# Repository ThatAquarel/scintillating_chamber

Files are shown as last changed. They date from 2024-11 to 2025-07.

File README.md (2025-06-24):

# [Dawson HEP](https://youtu.be/Yp-H1ZBjPuM)

Introduction Video:

Demo video (https://youtu.be/Yp-H1ZBjPuM)

## About us

Icons

**The Dawson High Energy Physics** club, run by Dr. Manuel Toharia Zapata is a place for curious college students to learn more about particle physics. Every week, students from a wide variety of programs meet to learn and discuss about flavour physisc, extra dimensions and much more. We engage with both theory and experiments, learning about and observing particles. Our many projects include an Alpha particle detector, spark chamber, Scintillating Chamber, and more.

Here's a [video](https://youtu.be/Yp-H1ZBjPuM) about our group!

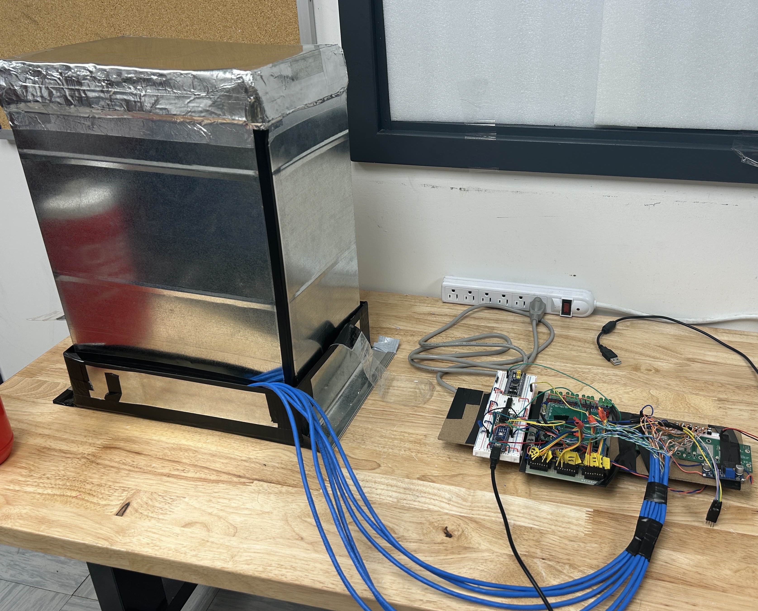
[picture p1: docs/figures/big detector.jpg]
Scintillating chamber


Our proposal to the 2025 [Beamline for schools](https://beamlineforschools.cern/) competition. It consists of an arrangement of scitillator rods to detect and model the trajectory of cosmic ray in three dimensions. The possible trajectories are then calculated and displayed graphically to the user.

**See Paper [HERE](./proposal/proposal.pdf)**

## Contacts

- Milo Belarbi
- David Birnbaum
- Tykhon Byshkin
- Matvey Chirchikov
- Danah Dézémé
- Arij Mohamedi
- [Evan Parasol](https://github.com/TheBookwyrms), blackdragon6493@gmail.com
- [Leandro Perez-Moran](https://github.com/LudioRex), pemle2007@gmail.com
- Ari Polterovich
- [Tian Yi, Xia](https://github.com/ThatAquarel), xtxiatianyi@gmail.com
- [Andy Yu](https://github.com/Anodymous1), andy.yu@dawsoncollege.qc.ca
- [Aljoscha Ziegler](https://github.com/Questionning), ziegleraljoscha@gmail.com

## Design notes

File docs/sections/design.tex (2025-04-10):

The general working principle of our detector is simple:
polyvinyl toluene (PVT) scintillator rods are arranged in
the detector, and when a muon passes through a rod, photons emitted are then detected by a Silicon Photomultiplier
(SiPM). The collected data is then transferred to a computer where the data is processed and rendered to display the possible paths of the muon. Our design strays from conventional detectors when it comes to the arrangement of the scintillator rods. While typical detectors use a grid design, we opted for a design inspired by binary encoding (see figure \ref{fig0}). 

\begin{figure}[h]
    \centering
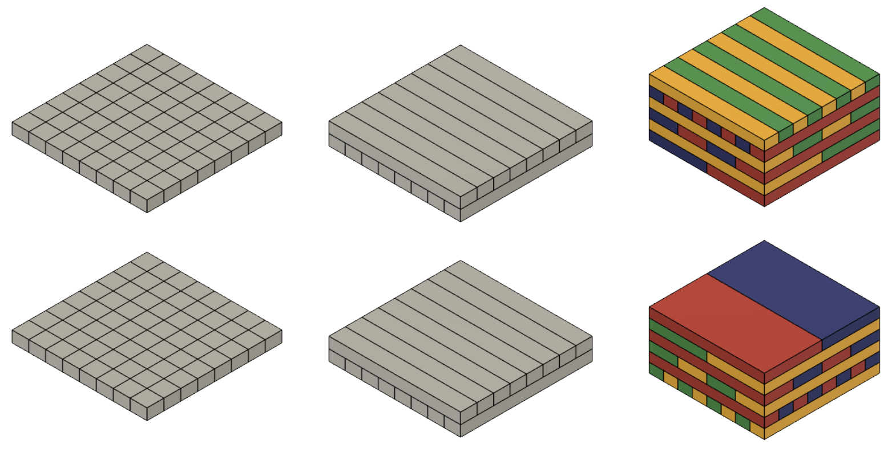
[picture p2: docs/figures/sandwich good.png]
    
\caption{Comparison of three scintillator placement methods: $n$ being the number of scintillators on the side of
one of the extreme layers. 
\textbf{Left:} One layer grid design. Number of sensors scale as $2n^2$.
\textbf{Middle:} Two layer grid design, scales as $4n$.
\textbf{Right:} Binary
encoding arrangement, number of required sensors scales as
$8 log_2(n)$. In each layer, identically coloured
scintillators are optically linked to the same SiPM by WLS
fiber.}
\label{fig0}
\end{figure}

This has two main benefits. First, it reduces the number of sensors needed, as only two sensors are necessary per layer. As such, the number of sensors needed for the detector increases logarithmically. Our design also allows for easy encoding of the detector’s state. With each layer only having two sensors, its state can be represented with a single bit, and because each layer is more specific than the previous, it narrows down the possible paths of the particle through the detector. Each set of signals therefore encodes for a specific pattern. This is analogous to the system used in the Apollo Guidance Computer’s rope core memory, with each bit representing an inhibit wire pair\cite{agc}.

\begin{figure}[h]
    \centering
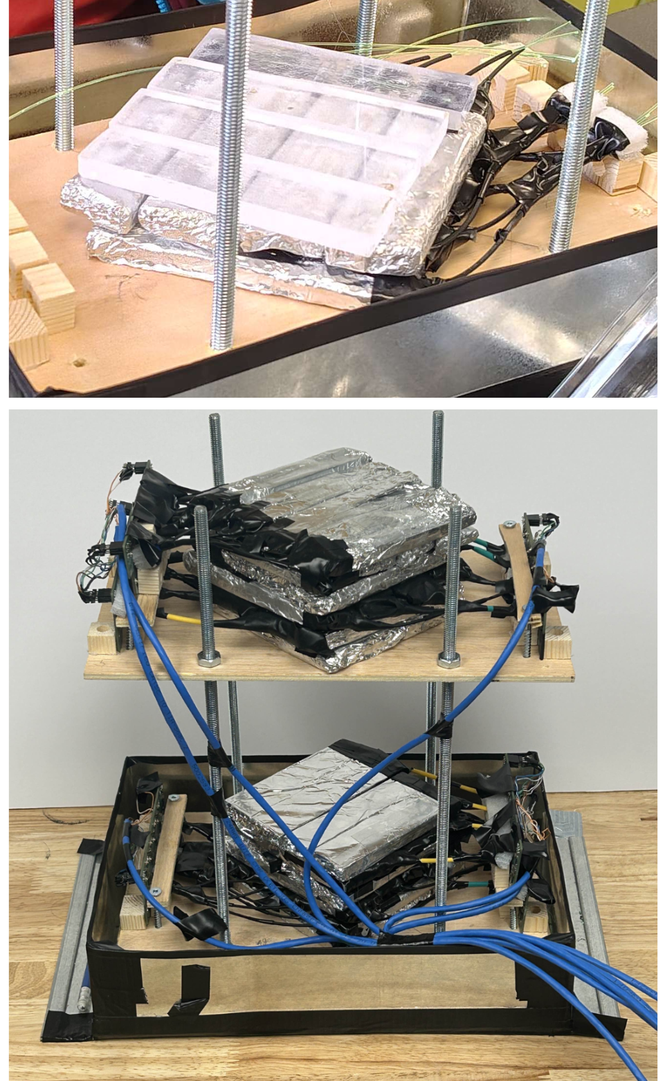
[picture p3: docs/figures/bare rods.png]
    
    \caption{Isometric view of physical detector. WLS fiber is encased within dark tubing toward the SiPM boards. Four threaded rods elevate the top platform: nuts allow for relative parallelism adjustment. Top and bottom scintillator packs permit the encoding of XY positioning; both combined, 3D trajectory tracking. A total of $12\,\text{layers} \times 2\,\text{SiPMs/layer} = 24\,\text{SiPMs}$.}
    \label{fig1}
\end{figure}

%\clearpage

\vspace{10mm}
In greater detail, each rod is optically isolated from its neighbors with aluminium foil and connected to a remote SiPM through wavelength shifting fiber (WLS fiber)\cite{wls} . We opted for WLS fiber, as is common among scintillation detectors, because it is more efficient at capturing the photons emitted by the scintillators than clear fibers. The output of the SiPMs being too weak, we use op-amp transimpedance amplifiers to amplify the signal. After being amplified, the signals are digitized before entering an FPGA circuit for fast acquisition \footnote{All circuits and PCBs are custom-made. Access the documentation \href{https://github.com/ThatAquarel/hep/tree/main/scintillator_field/hardware/docs}{\underline{here}}}. An Arduino then filters the signal before it is sent to a computer for processing.

\begin{figure}[h]
    \centering
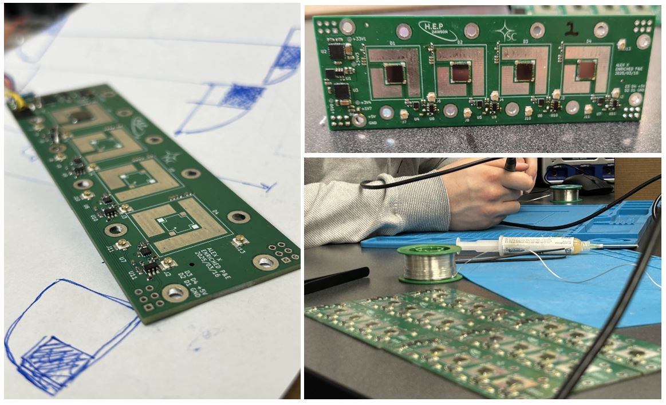
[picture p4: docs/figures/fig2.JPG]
    
\caption{Student-designed SiPM printed-circuit boards. Each PCB has four channels; a total of six PCBs are used in our detector. SiPMs and other components are manually populated onto the PCB.}
\label{fig2}
\end{figure}

%BIG BOX
\begin{figure} [h]
    \centering
    
    \caption{Binary optical encoding scintillation detector in its final form. \textbf{Left:} Light-tight faraday cage containing the detector made of HVAC conduit\textemdash decreasing light contamination and electrical noise. \textbf{Right:} Acquisition circuit linked with data cables.}
    \label{fig4}
\end{figure}

\vspace{15mm}
The trajectory volume\textemdash the possible volume of muon trajectory\textemdash is calculated in O(n) using Python code\footnote{All code can be found in our \href{https://github.com/ThatAquarel/hep}{\underline{GitHub repository}}.} by splitting the detector into two side-projections. The code calculates the trajectory volume projection for each side view by iterating over two levels at a time and conserving the tightest projection, first combining the center levels and finally the uppermost and lowermost levels. The volume trajectory projections are combined into the volume trajectory. Future updates will include : adapting to situations where the muon passed between two rods of the same level and taking advantage of situations where muons had to pass in between same level rods. 

\begin{figure}[h]
    \centering
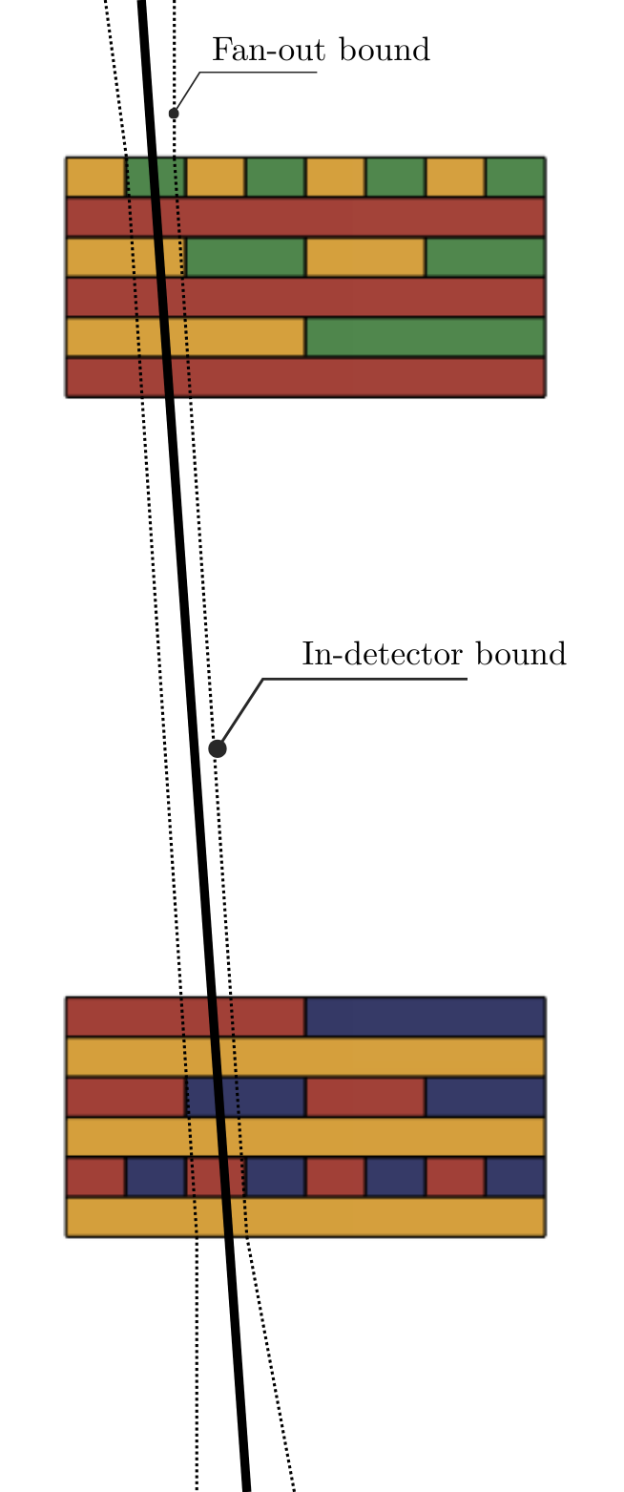
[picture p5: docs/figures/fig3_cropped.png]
    
    \caption{Representation of a possible muon trajectory and the calculated trajectory volume projection. Black line a possible muon path. Black dotted line is the side muon volume projection: boundaries for all possible muon paths.
}
    \label{fig3}
\end{figure}

The display is written in Python, using GLFW to create the display window, PyOpenGL to turn the coordinates from the muon volume trajectory into coordinates relevant to the computer, as well as to create the shaders, vertex arrays, and vertex buffers which are needed to render the scintillator structure and trajectory volume to the computer, and ImGui to create the text box that gives information to users.
\begin{figure}[h]
    \centering
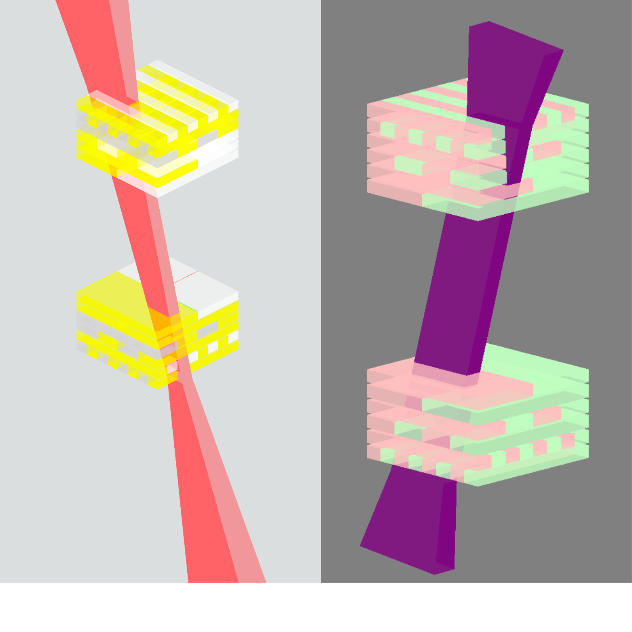
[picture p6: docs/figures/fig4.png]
    
    \caption{Two experimental instances of isometric views of binary positional decoding by our software from real data. \textbf{Left:} Signals sent to the computer are interpreted visually. \textbf{\textit{Yellow:}} Triggered scintillators. \textbf{\textit{White:}} Untriggered scintillators. \textbf{\textit{Red:}} Volume of possible muon trajectory resulting from binary elimination of trajectories. \textbf{Right:} More efficient render without signal interpretation. \textbf{\textit{Purple:}} Volume of possible muon trajectories.}
    \label{fig4}
\end{figure}

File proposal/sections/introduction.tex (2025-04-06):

At any given moment, there are muons raining down on us at a rate of approximately 1 muon per square centimeter per minute [1]. Traditionally, they are observed with the use of a spark chamber. However, building a spark chamber is a technical challenge, especially for high school students. We wanted to create a simple and easily reproducible way of observing muons, which is what led us to develop our three-dimensional scintillator-based detector, a.k.a. The Scintillating Chamber. Although we have developed the detector’s software and hardware components, precise calibration would require exposure to a controlled muon beam. Access to CERN’s world-class facilities would allow us to validate our detector’s performance and refine its accuracy. It would also provide invaluable insights into innovative techniques that would contribute to the broader field of particle detection technology. We hope to collaborate with peers and experts at CERN to deepen our comprehension of physics concepts through real-world applications. We are also committed to inspiring other young Canadian scientists by sharing our experiences and findings through outreach activities. An opportunity to conduct our experiment at CERN would be a pivotal step in this journey. We hope that our design can be used in physics classrooms around the world to assist science education and communication. Our team hopes to continue development to enhance our detector for these purposes, adding a timing device to measure the energy of the detected particles, and creating a better user interface for easier use in classrooms.

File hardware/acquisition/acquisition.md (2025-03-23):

# Acquisition

STM32F411CEU6

https://jlcpcb.com/partdetail/Stmicroelectronics-STM32F411CEU6/C60420

https://www.youtube.com/watch?v=aEwwQMdKd-c&t=1s&ab_channel=Phil%E2%80%99sLab

https://www.digikey.ca/en/products/detail/gct/USB4085-GF-A/9859662
`https://www.digikey.ca/en/products/detail/stmicroelectronics/USBLC6-2SC6/1040559

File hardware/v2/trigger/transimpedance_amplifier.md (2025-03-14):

# Transimpedance Amplifier Design Information

## Datasheets

https://www.analog.com/media/en/technical-documentation/data-sheets/18067fc.pdf

https://www.ti.com/lit/ds/symlink/opa855.pdf

## References

https://www.analog.com/en/resources/technical-articles/stabilize-transimpedance-amplifier-circuit-design.html

https://www.ti.com/lit/an/sboa268b/sboa268b.pdf?ts=1741505795019

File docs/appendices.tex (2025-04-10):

\begin{figure} [h]
    \centering
    
    \caption{\textbf{Top:} Signal acquisition circuit. \textbf{\textit{Left:}} Low-noise 5\,V power supply for all SiPM PCB boards (TPS7A470, $4\,\mu\text{V}_\text{RMS}$). \textbf{\textit{Middle:}} 24-channel digital signal reader with FPGA (ICE40HX1K), 5\,V to 3.3\,V level shifters, and indicator LEDs associated with each SiPM sensor. \textbf{\textit{Right:}} Breadboard: Arduino Nano for serial data communication over USB to the computer, and STM32F103C for clock signal generation. \textbf{Bottom left:} Work in progress FPGA detector module. \textbf{Bottom right:} Manual soldering of individual wires for the 24 LED indicators.}
    \label{fig5}
\end{figure}

\begin{figure}[h] 
    \centering 
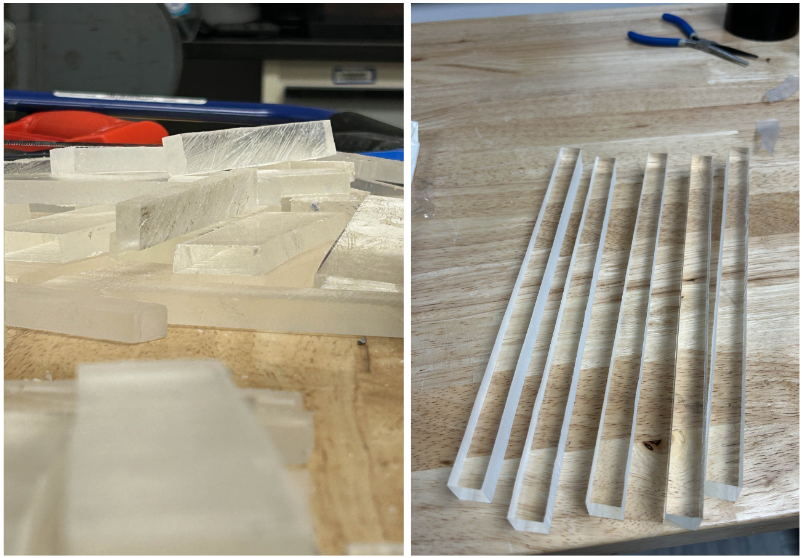
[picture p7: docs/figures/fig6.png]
    
    \caption{Scintillator rods cut with a bandsaw from a larger
scintillator block. Two $500\times250\times30$ mm BC408 PVT scintillators were graciously offered to us by McGill Professor Dr. David Hanna\textemdash which we then proceeded to cut and polish manually.}
    \label{fig6}
\end{figure}

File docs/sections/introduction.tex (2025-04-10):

At any given moment, there are muons raining down on us at a rate of approximately 1 muon per square centimeter per minute \cite{Spectrum of CRM,hyperphysics,atmospheric muon,pdg}. 
Traditionally, spark chambers or wire chambers allow the tracking of muon trajectories. However, building a high voltage chamber is a technical challenge, especially for high school students and for their mentors worrying about safety. We wanted to create a simple, safe and easily reproducible way of observing muons, which is what led us to develop our three-dimensional scintillator-based detector, a.k.a. The Scintillating Chamber.

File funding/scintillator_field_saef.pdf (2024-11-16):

# Scintillator Field Elementary Particle Detector

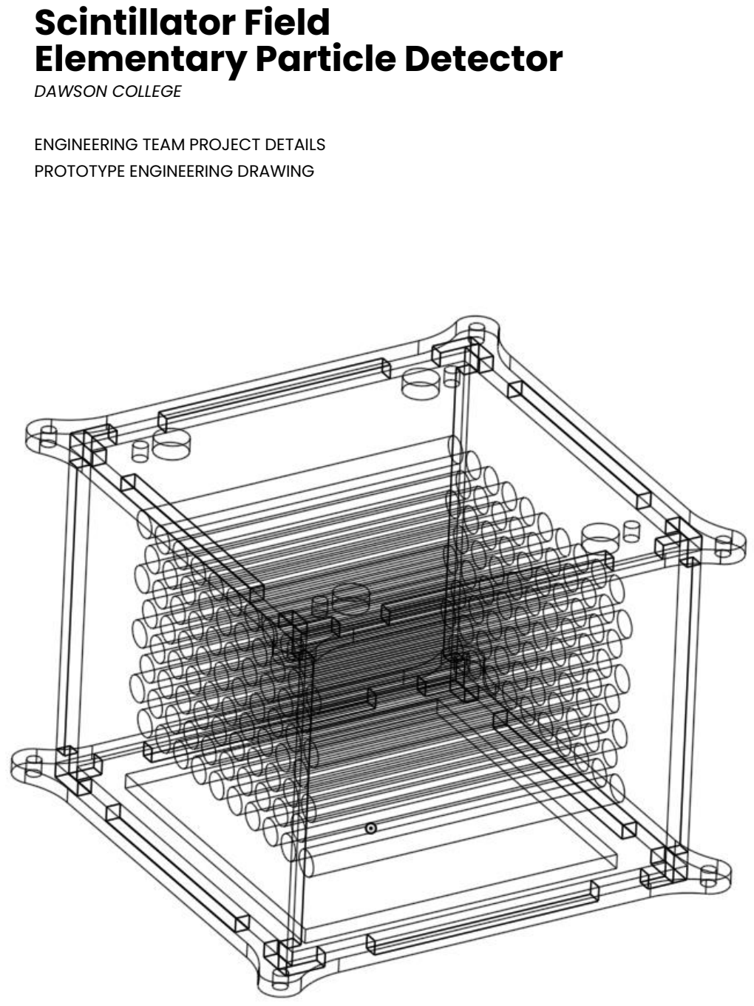
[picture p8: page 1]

DAWSON COLLEGE

ENGINEERING TEAM PROJECT DETAILS PROTOTYPE ENGINEERING DRAWING

### Contents

### Project description

We submit our project to the Beamline for Schools international competition at CERN. It is completed as a part of Dawson’s High Energy Particle Physics Club.
In order to concretize our design by means of effective teamwork, we have split the execution of our project into several sub-tasks. We have a hardware engineering team, a software team, a math pattern optimization team, a theoretical particle physics research team and a directing team.
1. The mathematics team has been working on the problem of optimizing rod placement for the highest accuracy on the greatest covered area. Further, they have been researching how to create a statistical field to determine particle position using concepts from linear algebra and Bayesian statistics.
2. The hardware team has come up with the concept of using scintillators with photomultipliers to detect muon position using a customized PCB system
3. The software team has been designing the system-workflow of the PCB's and the data analysis implementation of the statistical field that determines muon position.
4. The physics research team has concerned itself with verifying the feasibility of the endeavour and setting reasonable boundaries to expected particle position.
5. The directing team has done a wonderful job at coordinating everyone's work by keeping a general overview and ensuring everybody is on the same page.

### Current prototype

This is an example of the hardware team's first prototypes of a laser-cut acrylic case for our apparatus, along with aluminium supports. The goal of the case is to protect the internal system while allowing for very precise scintillator rod placements. The heatsinks of a high throughput cooling system required by our detector is shown (in black). This is only the support system for the actual detector rods, which we could not yet acquire. SAEF’s funding will support the purchase of the parts necessary to complete this machine.

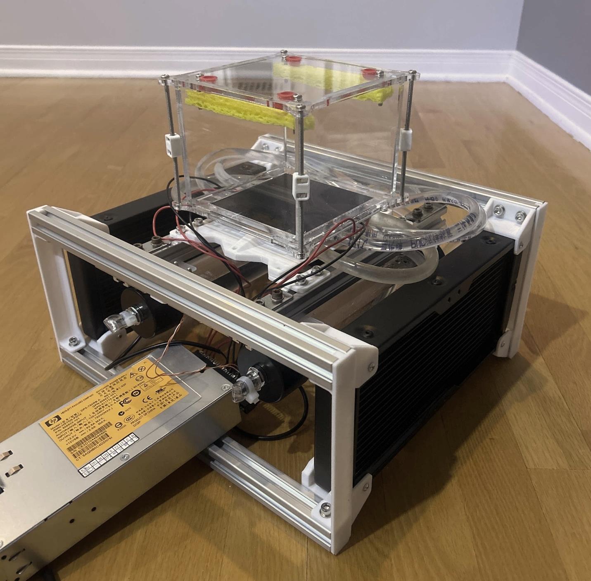
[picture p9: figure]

### Teamwork, Communication and Diversity

Here one of our members from the hardware team is designing a first computational model of the case that will be able to hold 3d printed parts that will keep the rods in place (left).
The lead of the mathematics team is explaining his simulation to someone from our hardware team so that the hardware team is aware of which rod arrangement models their case has to be able to hold (right).

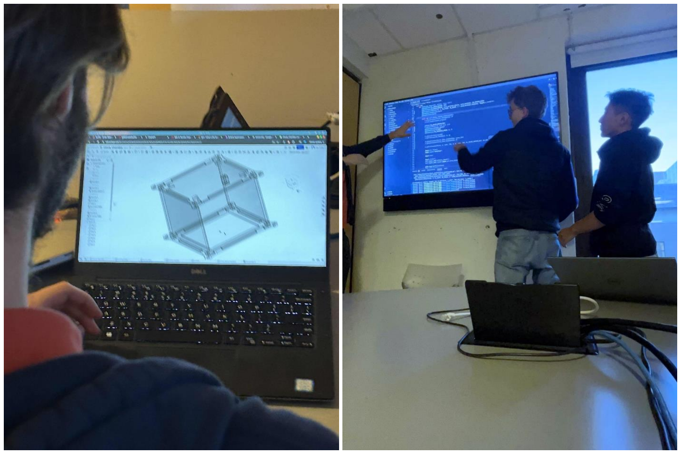
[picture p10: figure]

Here is an image of two the PCBs’ our software team has been getting acquainted with. They will implement their final code as soon as the mathematics team has chosen an optimal pattern and that the physics team approves the pattern as feasible with confirmation from our hardware teammates.

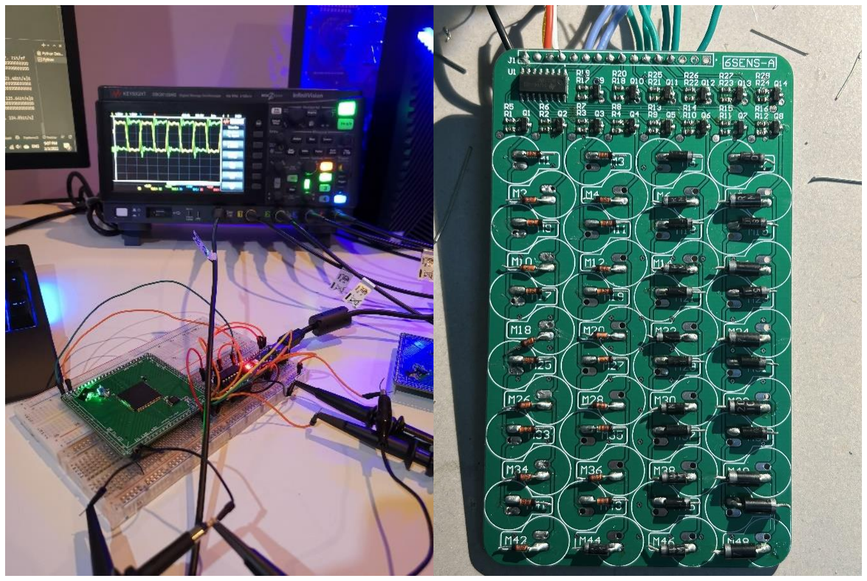
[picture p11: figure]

### Iterative Designs

Here is an image of the hardware team’s construction and engineering process to attain the cryogenic temperatures required for our detector’s functioning. The construction was done in steps to ensure each part works separately before integration: 3D printing, water-cooling and wiring. This consists of the support structures necessary for the rods – the rest of our approach – to work properly. Our hardware team is currently working on iterating on these designs, as well as modeling them before physical construction.

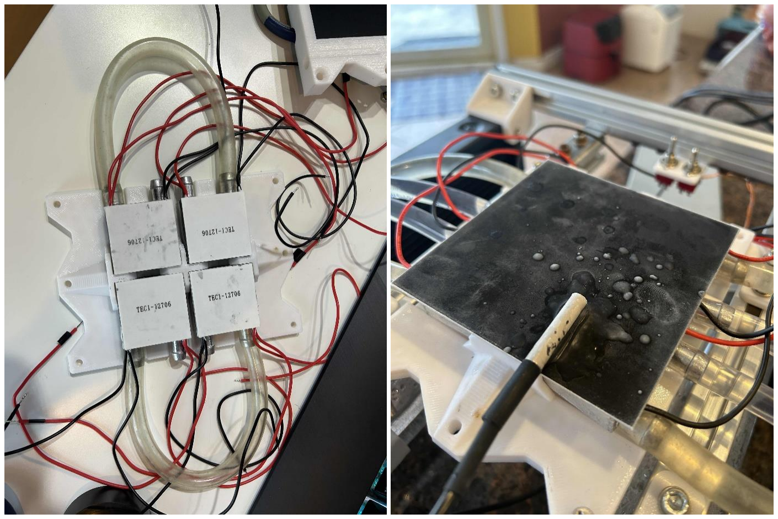
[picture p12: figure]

### Finances and Supplies

We detail the listed supplies in the “Projects Costs” section of the application here. These parts we could not yet purchase, but they are critical in the working of the detector.

Plastic scintillator rods | 128 x 19.13 $ + tx = 2815.32 $
5mm in diameter, 100mm in length: the scintillator rods emit light when a subatomic particle intersects its volume. This is a critical dependency in terms of supplies, as our particle detection approach relies on their properties.
Supplier: https://eljentechnology.com/
Silicon photomultipliers | 128 x 22.44 $ + tx = 3302.45 $
6mm by 6mm microchips: the silicon photomultipliers amplify the light emissions from the rods, and convert them into measurable electronic pulses.

Supplier: www.mouser.ca

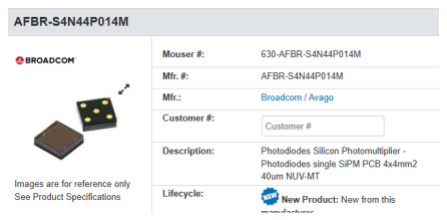
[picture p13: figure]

Aluminium Extrusion Bars | 1 set for the case + tx = 22.97 $
20mm by 20mm in cross-section aluminium bars for general support.

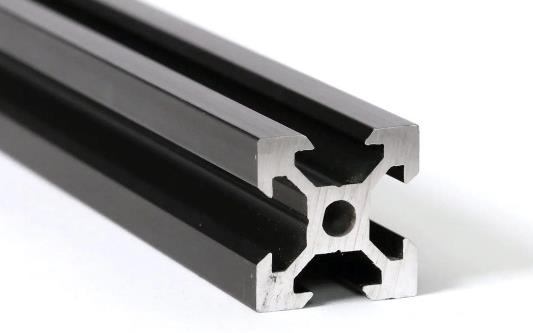
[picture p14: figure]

Supplier: www.mcmaster.com

Printed Circuit Boards | 16 PCBs x 2.57$ + tx =47,28 $
Electronic Components (miscellaneous) | 100 $
The printed circuit board is the design of our hardware team, and the manufacturing will be done via an online service. They will reliably connect our electrical components, and make sure our detector functions properly. We allocate a budget of 100$ for the electric components since there are many contained within the parts list. Here’s an example of the PCB that will analyze the signals emitted by the silicon photomultipliers.

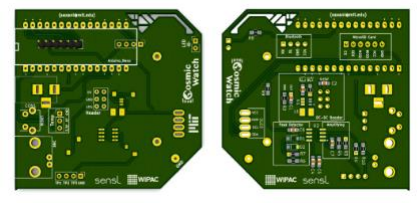
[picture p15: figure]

Supplier: https://jlcpcb.com/

3D Printing Material | 2kg x 22.76$/kg + tx = 52.34 $
Parts designed by our hardware team that need to be rapidly manufactured will be made in-house on 3D printers. Consequently, the rolls of PLA plastic required will be an expense. Our existing 3D printer that we will use for prototyping parts.

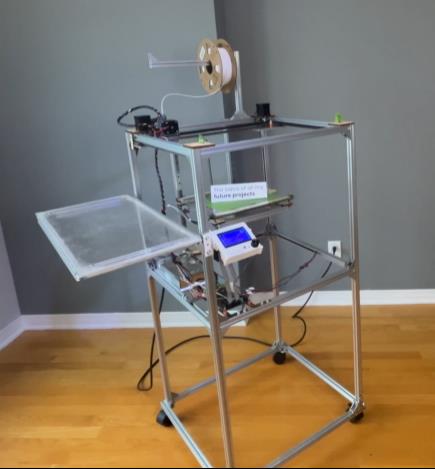
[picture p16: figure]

Supplier: https://polymaker.com/

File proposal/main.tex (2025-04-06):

\documentclass[12pt]{article}
\usepackage{graphicx}   % Required for inserting images.
\usepackage{amsmath, amssymb, gensymb}  % Required for advanced formula formatting.
\usepackage{float}  % Required to force figure position.
\usepackage{authblk}    % Required for authors and affiliation formatting.
\usepackage{multicol}   % Required for making document two-column.
\usepackage{lipsum} % Temporary package for blind text.

\title{Calibrating a three-dimensional scintillator-based muon detector}

\author{Tian Yi Xia}
\author{Aljoscha Ziegler}
\author{Leandro Perez Moran}
\author{Evan Parasol}
\author{Andy Yu}
\author{Milo Belarbi}
\author{[Placeholder]}  % The list of authors is not complete

\affil{Dawson College, Canada}
\date{April 10, 2025}   

\begin{document}

\maketitle

\begin{multicols}{2}

\section{Introduction}
\input{sections/introduction}

\section{Design}
\input{sections/design}

\section{Results}
\input{sections/results}

\section{Experiment}
\input{sections/experiment}

\section{Community outreach}
\input{sections/community_outreach}

\end{multicols}

% Section: Acknowledgements
\input{acknowledgements}

\end{document}

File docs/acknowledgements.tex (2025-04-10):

We would like to sincerely thank Dr. Manuel Toharia for his dedication to the High Energy Particle Physics group at Dawson, for his captivating lectures and for his guidance throughout our project. We are incredibly grateful to McGill University Professor Dr. David Hanna for his invaluable advice and for graciously letting us use his scintillator block as well as McGill University Professor Dr. François Corriveau for his guidance. We express our sincere appreciation to Université de Montréal technician Dr. Nikolai Starinsky for his scintillator cutting advice. This project would not have been possible without the Dawson Foundation’s Student Academic Growth and Enrichment Fund, whose grant provided money with which we bought power tools, safety equipment, and electronics. Finally, we would like to express our gratitude to Dawson College for offering us a wonderful learning environment that allowed us to flourish and engage in science activities that we are passionate about.

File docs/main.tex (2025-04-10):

\documentclass[aps,prl,reprint,groupedaddress]{revtex4-1}
\usepackage{graphicx}    % Required for inserting images.
\usepackage{amsmath,amssymb,gensymb}  % Advanced math formatting.
\usepackage{float}  % Required to force figure position.
\usepackage{lipsum} % For dummy text.
\usepackage{hyperref}

\begin{document}

\title{Calibration of a Three-dimensional Muon Detector Based on Scintillator Binary Optical Encoding\\[0.5ex] \small Team Dawson Technicolor}

\author{Milo Belarbi}
\author{David Birnbaum}
\author{Tykhon Byshkin}
\author{Matvey Chirchikov}
\author{Danah Dézémé}
\author{Arij Mohamedi} 
\author{Evan Parasol}
\author{Leandro Perez Moran}
\author{Ari Polterovich}
\author{Tian Yi Xia}
\author{Chun On Yu}
\author{Aljoscha Ziegler}
\author{Manuel Toharia}
\altaffiliation{Teacher}
\author{Joel Trudeau}
\altaffiliation{Teacher}

\affiliation{Dawson College, Montreal, Quebec, Canada}
\date{April 10, 2025}

\maketitle

%\begin{multicols}{2}

\section{Introduction}
\input{sections/introduction}

\section{Design}
\input{sections/design}

\vspace{40mm}
\section{Results}
\input{sections/results}

%\clearpage

\section{Experimental Proposal}
\input{sections/experiment}

\section{Outlook}
\input{sections/conclusion}

%TC:ignore
\section{Community outreach}
\input{sections/community_outreach}

%\end{multicols}

% Section: Acknowledgements
%\clearpage
\section{Acknowledgments}
\input{acknowledgements}

\clearpage
\section{Appendices}
\input{appendices}

\begin{thebibliography}{99}
% \cite{Spectrum of CRM}
\bibitem{Spectrum of CRM}
Gardner, M., et al., "The Momentum Spectrum of Cosmic Ray Muons near Sea Level in the Momentum Range 0.4--10 GeV/c." IOPScience. Accessed March 2022,
\url{https://iopscience.iop.org/article/10.1088/0370-1328/80/3/314/pdf}.

% \cite{hyperphysics}
\bibitem{hyperphysics}
Hyperphysics, "Atmospheric Muons." Georgia State University. Accessed March 2022,
\url{http://hyperphysics.phy-astr.gsu.edu/hbase/Particles/muonatm.html}.

% \cite{atmospheric muon}
\bibitem{atmospheric muon}
CERN, "Cosmic Rays: Particles from Outer Space." Accessed March 2022,
\url{https://home.cern/science/physics/cosmic-rays-particles-outer-space}.

\bibitem{pdg}
K.~Nakamura \textit{et al.} [Particle Data Group], J. Phys. G \textbf{37}, 075021 (2010),
doi:10.1088/0954-3899/37/7A/075021,
\url{https://pdg.lbl.gov/2011/reviews/rpp2011-rev-cosmic-rays.pdf}.

\bibitem{agc}
Kuttner, P. The rope memory: a permanent storage device. {\em Proceedings Of The November 12-14, 1963, Fall Joint Computer Conference}. pp. 45-57 (1963), \url{https://doi.org/10.1145/1463822.1463829}

\bibitem{wls}Worstell, W., Doulas, S., Johnson, O. \& Lin, C. Scintillator crystal readout with wavelength-shifting optical fibers. {\em Proceedings Of 1994 IEEE Nuclear Science Symposium - NSS'94}. \textbf{4} pp. 1869-1873 vol.4 (1994)
\url{https://dl.acm.org/doi/pdf/10.1145/1463822.1463829}

\end{thebibliography}
%TC:endignore

\end{document}

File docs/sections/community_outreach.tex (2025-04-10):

Women, though largely unrecognized, have played a great role in the development of modern science. Marie Curie, Ada Lovelace, Katherine Johnson, and many others have been role models for generations of scientists. Our team at Dawson TECHNICOLOR firmly believes that part of promoting science education is promoting the inclusion of women and other marginalized groups. As such, we are currently working with Dawson STEMM FEM, a local club, to create talks and participate in events that will hopefully encourage many young women to join the beautiful field of physics and of science as a whole.

Furthermore, The Scintillating Chamber is set to be presented in May at Dawson’s ScienceFest. This event consists of a fair where a myriad of scientific projects are introduced to the student body. This opportunity will allow us to make particle physics more accessible and easier to grasp while sharing our unwavering passion.

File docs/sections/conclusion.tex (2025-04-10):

We have fully developed the detector’s software and hardware components on our own. Therefore, precise calibration would require exposure to a controlled muon beam. Further, a controlled muon beam would permit us to test out features we are currently developing such as measuring the detection time and using a time-over-threshold system to find the energy of muons passing through the detector. Access to CERN’s facilities would allow us to validate our detector’s performance and refine its accuracy.

The confirmation of the viability at CERN of our safety-oriented detector design allows for open-sourcing, along with physics classroom outreach—projects with which we align. We believe that getting this detector ready for research will inspire more students to design their own particle physics experiments.

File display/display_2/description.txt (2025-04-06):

app.py
    -This is the file where you run the code. 
    -All of the draw functions(including the gui) are called here. 
        There's a rendering_loop function which calls the on_render_frame.
        The on_render_frame function calls the draw function in each class found in the elements folder.
    -All of the input functions can also be found here.
        processes mouse clicks to be used for display

test.py
    -This is where all of the data points come from. 
    -The algorithm designed by Aljoscha gives out vertices for drawing objects
    -The code allows one to have multiple "datasets". This means that:
        You can toggle multiple datasets at once from the ui
        Each dataset can be displayed seperately, meaning that they can overlap and you can display whichever datasets you want
        You can have multiple points within the dataset
        This is why we have this monstrosity of a list:

        test.data
            |_ datasets
                |
                |_ cubes/prisms/points(whatever you want to call it)
                    |
                    |_ vertices
                    |    |
                    |    |_(x,y,z) coordinates
                    |
                    |_ fanning pairs
                    |    |
                    |    |_ pairs: (1-8), (2-7), (3-6), (4-5)
                    |        |
                    |        |_ vertices (eg 1)
                    |            |
                    |            |_ (x,y,z)
                    |
                    |_ raw data(original binary)

arduino.py
    -Code to retrieve data from the arduino chip

graphics

    shaders
        -vertex.glsl, fragment.glsl

    orbit_controls.py
        -camera matrices, controls etc

    parameter_interface.py
        -imgui
        -user interface
        -toggles some variable in app.py to update the display
            e.g. self.show_axes, self.dataset_active
            pt_selected comes from app.py
        -test passes some info into the class to display
            (in particular, test.data)

    shader_renderer.py
        -"Shader Renderer: Accelerates via GPU lighting computations
        and rendering of frames, and sets up the drawing context
        necessary for OpenGL to function"

    vbo.py
        -functions from this file is used to draw
        -create_vao, draw_vao and update_vbo are called in every file in the folder "elements"
            -each file in elements first computes the first set of data and calls create_vao
            -in each rendering loop, the draw function inside the element calls update_vbo and draw_vao for the display

    elements
        -All of these classes are created in app.py(__init__ function)
        -there is a draw function in each of the classes in each elements file
            -it draws the object provided the vertices of the triangles
            -the draw function is called in the on_render_frame function in app.py

        axes.py
            -toggles the x-y-z axes 
            -for the convenience of testing

        fan.py
            -creates the fanning for each data point

        plane.py
            -creates the scintillator rods

        square.py
            -creates the datapoint cubes

        trajectory.py
            -connects consecutive data points together to show a trajectory
            -used in previous versions of the code

        cube.py
            -template sort of thing
            -no longer in use

test(me).py and test_data.py
Outdated
For testing in previous versions of the code

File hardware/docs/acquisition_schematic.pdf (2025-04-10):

IOR_72 | 107 BANK ¹
IOL_12A | 33 IOL_12B | 34 BANK ³

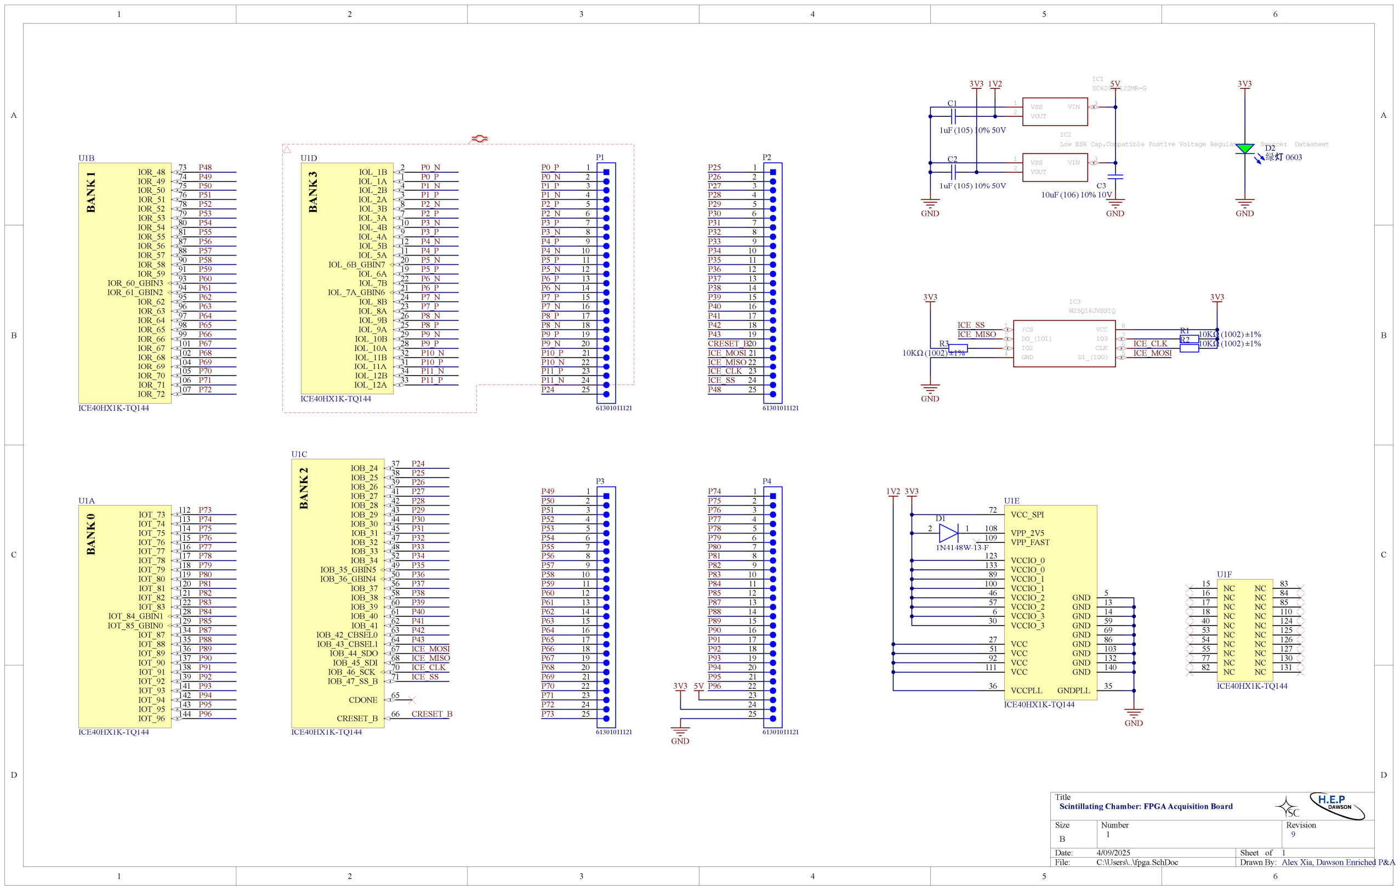
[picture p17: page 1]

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
Title

Size | Number | Revision
B
Date: | 4/09/2025 | Sheet of
File: | C:\Users\..\fpga.SchDoc | Drawn By:

VSS 1
VOUT 2

VIN 3

IC2
Low ESR Cap.Compatible Postive Voltage Regulators Source: Datasheet

GND

3V3 | 5V 1V2

C3
10uF (106) 10% 10V

GND

C2

1uF (105) 10% 50V

C1

1uF (105) 10% 50V

/CS 1
DO_(IO1) 2
IO2 3
GND 4
VCC | 8
IO3 | 7
CLK | 6
DI_(IO0) | 5

IC3
W25Q16JVSSIQ

GND

3V3 | 3V3

R1 10KΩ (1002) ±1%
R3
10KΩ (1002) ±1%

R2 10KΩ (1002) ±1%
ICE_MOSI

ICE_SS
ICE_MISO
ICE_CLK

D2 绿灯 0603

3V3

GND

VSS 1
VOUT 2

VIN

3

IC1
XC6206P122MR-G

2 1

D1

1N4148W-13-F

GND

1V2 3V3

IOT_73 | 112
IOT_74 | 113
IOT_75 | 114
IOT_76 | 115
IOT_77 | 116
IOT_78 | 117
IOT_79 | 118
IOT_80 | 119
IOT_81 | 120
IOT_82 | 121
IOT_83 | 122
IOT_84_GBIN1 | 128
IOT_85_GBIN0 | 129
IOT_87 | 134
IOT_88 | 135
IOT_89 | 136
IOT_90 | 137
IOT_91 | 138
IOT_92 | 139
IOT_93 | 141
IOT_94 | 142
IOT_95 | 143
IOT_96 | 144 BANK ⁰

U1A

ICE40HX1K-TQ144

IOR_48 | 73
IOR_49 | 74
IOR_50 | 75
IOR_51 | 76
IOR_52 | 78
IOR_53 | 79
IOR_54 | 80
IOR_55 | 81
IOR_56 | 87
IOR_57 | 88
IOR_58 | 90
IOR_59 | 91
IOR_60_GBIN3 | 93
IOR_61_GBIN2 | 94
IOR_62 | 95
IOR_63 | 96
IOR_64 | 97
IOR_65 | 98
IOR_66 | 99
IOR_67 | 101
IOR_68 | 102
IOR_69 | 104
IOR_70 | 105
IOR_71 | 106

U1B

ICE40HX1K-TQ144

IOB_24 | 37
IOB_25 | 38
IOB_26 | 39
IOB_27 | 41
IOB_28 | 42
IOB_29 | 43
IOB_30 | 44
IOB_31 | 45
IOB_32 | 47
IOB_33 | 48
IOB_35_GBIN5 | 49
IOB_36_GBIN4 | 50
IOB_34 | 52
IOB_37 | 56
IOB_38 | 58
IOB_39 | 60
IOB_40 | 61
IOB_41 | 62
IOB_42_CBSEL0 | 63
IOB_43_CBSEL1 | 64
CDONE | 65
CRESET_B | 66
IOB_44_SDO | 67
IOB_45_SDI | 68
IOB_46_SCK | 70
IOB_47_SS_B | 71 BANK ²

U1C

ICE40HX1K-TQ144

IOL_1A | | 1
IOL_1B | | 2
IOL_2A | | 3
IOL_2B | | 4
IOL_3A | | 7
IOL_3B | | 8
IOL_4A | | 9
IOL_4B | | 10
IOL_5A | 11 IOL_5B | 12
IOL_6A | 19 IOL_6B_GBIN7 | 20
IOL_7A_GBIN6 | 21 IOL_7B | 22
IOL_8A | 23 IOL_8B | 24
IOL_9A | 25 IOL_9B | 26
IOL_10A | 28 IOL_10B | 29
IOL_11A | 31 IOL_11B | 32

U1D

ICE40HX1K-TQ144

GND 5

VCCIO_3 6

GND | 13
GND | 14

VCC 27

VCCIO_3 30

GNDPLL 35 VCCPLL 36

VCCIO_2 46

VCC 51

VCCIO_2 57

GND | 59
GND | 69

VCC_SPI 72

GND 86

VCCIO_1 89

VCC 92

VCCIO_1 100

GND 103

VPP_2V5 108
VPP_FAST 109

VCC 111

VCCIO_0 123

GND 132

VCCIO_0 133

GND 140

U1E

ICE40HX1K-TQ144

NC 15
NC 16
NC 17
NC 18
NC 40
NC 53
NC 54
NC 55
NC 77
NC 82
NC | 83
NC | 84
NC | 85
NC | 110
NC | 124
NC | 125
NC | 126
NC | 127
NC | 130
NC | 131

U1F

ICE40HX1K-TQ144

P0_N
P0_P
P1_N
P1_P
P2_N
P2_P
P3_N
P3_P
P4_N
P4_P
P5_N
P5_P
P6_N
P6_P
P7_N
P7_P
P8_N
P8_P
P9_N
P9_P
P10_N
P10_P
P11_N
P11_P

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
ICE_MOSI
ICE_MISO
ICE_CLK
ICE_SS

CRESET_B

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
P0_P
P0_N
P1_P
P1_N
P2_P
P2_N
P3_P
P3_N
P4_P
P4_N
P5_P
P5_N
P6_P
P6_N
P7_P
P7_N
P8_P
P8_N
P9_P
P9_N
P10_P
P10_N
P11_P
P11_N
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
CRESET_B
ICE_MOSI
ICE_MISO
ICE_CLK
ICE_SS

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
61301011121

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
61301011121

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
61301011121

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
61301011121
GND

3V3 5V

Scintillating Chamber: FPGA Acquisition Board

1 9

1
Alex Xia, Dawson Enriched P&A

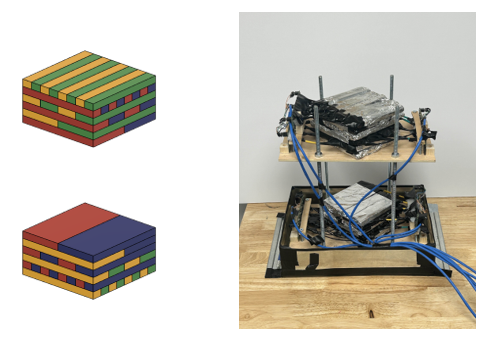
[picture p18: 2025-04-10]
docs/figures/fig1.png

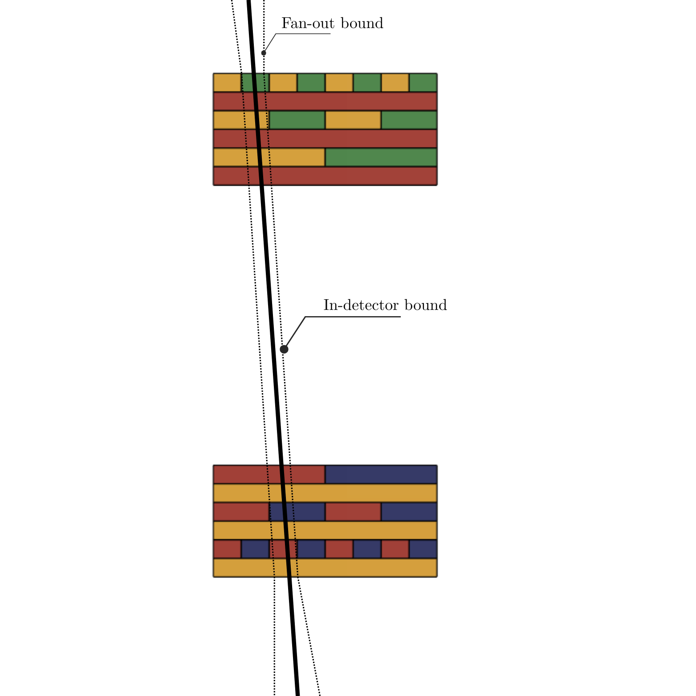
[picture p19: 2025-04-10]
docs/figures/fig3.png

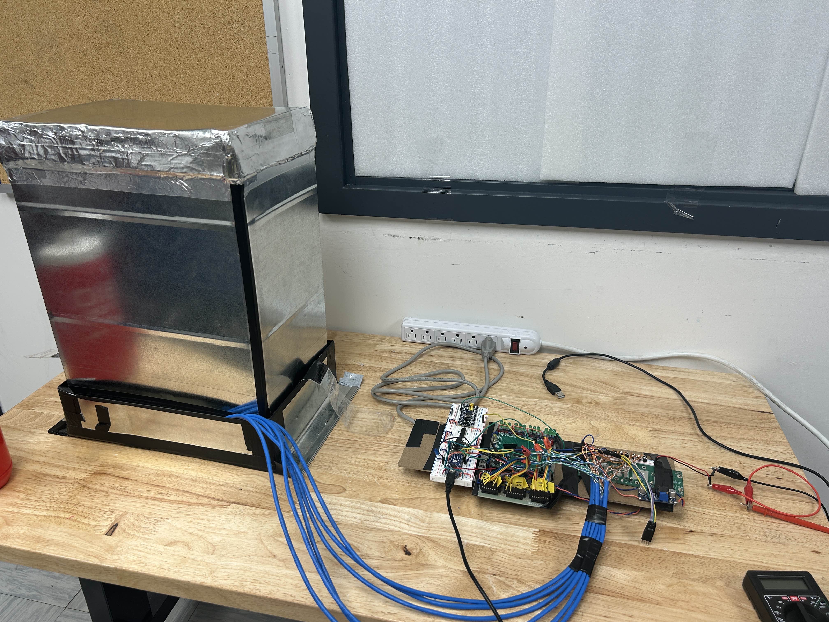
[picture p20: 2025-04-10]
docs/figures/fig7.jpg

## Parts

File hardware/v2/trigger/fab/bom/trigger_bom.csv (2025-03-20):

Comment | Designator | Footprint | LCSC
22p, 50V | C1 | Capacitor_SMD:C_0402_1005Metric | C70464
10n, 50V | C11,C12,C13,C14,C15,C16,C17,C18,C19,C20,C21,C22,C23,C24,C25,C26,C37,C38,C39,C40,C47,C48,C49,C50 | Capacitor_SMD:C_0402_1005Metric | C1524
0.1u, 50V | C2,C31,C32,C33,C34,C41,C42,C43,C44 | Capacitor_SMD:C_0402_1005Metric | C1581
3p, 50V | C27,C28,C29,C30 | Capacitor_SMD:C_0402_1005Metric | C1564
1u, 50V | C3,C4,C5,C6,C8,C9 | Capacitor_SMD:C_0603_1608Metric | C15849
2.2u, 10V | C35,C36,C45,C46 | Capacitor_SMD:C_0402_1005Metric | C60078
10u, 50V | C7,C10 | Capacitor_SMD:C_1206_3216Metric | C13585
Conn_Coaxial_Small, I-PEX MHF1 | J2,J3,J4,J6,J7,J8,J10,J11,J13 | connectors:BWIPX-1-001E | C496552
22uH | L1 | lqh3npn:L_Murata_LQH3NPN_3.0x3.0mm | C237408
12k 0.1% | R1 | Resistor_SMD:R_0402_1005Metric | C317927
20R | R15,R16,R17,R18 | Resistor_SMD:R_0402_1005Metric | C25089
316k 0.1% | R2 | Resistor_SMD:R_0603_1608Metric | C861317
0R | R23,R24,R25,R26 | Resistor_SMD:R_0402_1005Metric | C17168
226k 0.1% | R3,R19,R20,R21,R22 | Resistor_SMD:R_0603_1608Metric | C861233
10k 0.1% | R4,R5,R6,R31,R32,R33,R34 | Resistor_SMD:R_0603_1608Metric | C136139
49.9R | R7,R8,R9,R10,R11,R12,R13,R14,R27,R28,R29,R30 | Resistor_SMD:R_0402_1005Metric | C25120
LT3461A | U1 | Package_TO_SOT_SMD:TSOT-23-6 | C481768
TPS7A4701 | U2,U3 | Package_DFN_QFN:Texas_RGW0020A_VQFN-20-1EP_5x5mm_P0.65mm_EP3.15x3.15mm_ThermalVias | C90084
OPA858xDSG | U4,U5,U6,U7 | Package_SON:WSON-8-1EP_2x2mm_P0.5mm_EP0.9x1.6mm | C970232
TLV3501AIDBV | U8,U9,U10,U11 | Package_TO_SOT_SMD:SOT-23-6 | C193413

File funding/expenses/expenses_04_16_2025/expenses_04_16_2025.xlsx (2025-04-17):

Expense Description | Item Receipt File | Paid by | Receipt & Invoice | Amount (CAD)
Main Tooling Equipment (Makerspace, 7A.4)
Compressor, saw, saw blade set, face masks from Home Depot |  | Aljoscha |  | 397.45
Electronic Materials
10x Rigid Populated printed circuit board from JLCPCB | a.pdf (in USD) a_invoice.png (in CAD) | Alex |  | 620.58
32x MICROFC-60035-SMT-TR Silicon Photomultipiers (SiPM) | b.pdf | Alex |  | 1345.77
 |  |  | TOTAL (Finances 04-16-2025) | 2363.80

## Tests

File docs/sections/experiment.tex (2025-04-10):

Our muon tracker is currently producing experimental results, but we have no way of confirming their validity. As such, we propose using CERN’s high-energy Proton Synchrotron as a source of a controlled muon beam and use this experiment to compare our detector tracking results with the known trajectory of the Proton Synchrotron muon beam.

The evaluation of XY translational accuracy will be assessed by aiming the detector’s Z axis toward the beamline and iterating through different XY positions; the evaluation of XYZ rotational accuracy will be done by iterating through diverse altitude and azimuth angles. As the position is encoded to an $8 \times 8$ grid, a minimum of 64 different translations and 64 rotations will confirm the correct triggering of all SiPMs and the faithfulness of the trajectory volume computation with the actual trajectories.
\begin{figure} [h]
    \centering
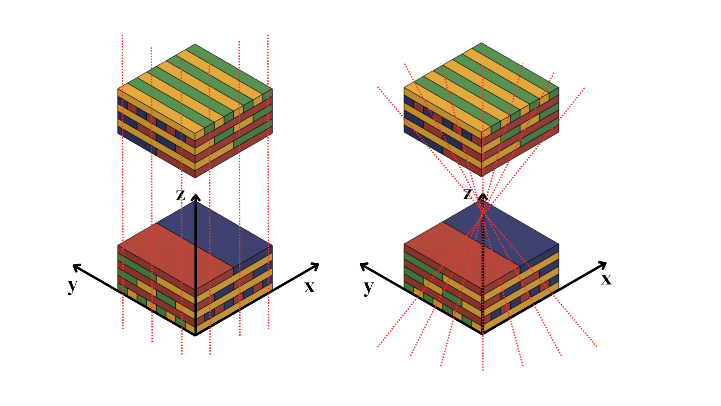
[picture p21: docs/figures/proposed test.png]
    
    \caption{Experimental proposal axes reference frame. \textbf{Left:} Example XY translational testing beamlines. \textbf{Right:} Example XYZ rotational testing beamlines.}
    \label{proposed tests}
\end{figure}

\begin{figure} [h]
    \centering
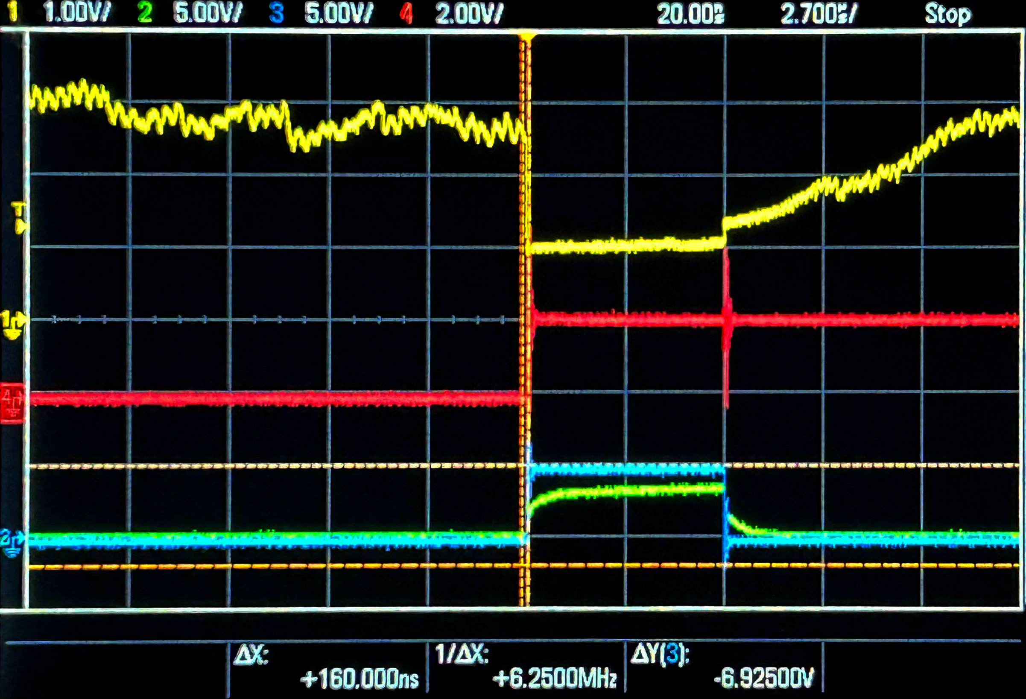
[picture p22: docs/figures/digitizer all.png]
    
    \caption{Digitizer circuit signals from acquisition hardware. \textbf{Yellow:} analog output from trans-impedance amplifier connected to comparator inverting input. \textbf{Red:} latching FPGA register for acquisition. \textbf{Blue:} comparator output. \textbf{Green:} level-shifted comparator output. Adjustable comparator threshold voltage: 1.133V $\pm$ 0.1\%.}
    \label{digitizer}
\end{figure}

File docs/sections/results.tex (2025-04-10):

After initial testing, we recorded several detections. The results were not affected by the intensity of light in the room, suggesting that the detector was successfully optically sealed.

The muon flux detected is around 2.5 hits/minute, lower than in theory. We believe that this is due to our conservative data filtering, and small field of view: we wanted to reduce the chances of introducing noise as much as possible. As such, the calibration of our detector is crucial to capture accurate trajectories.

%oscilloscope 1
\begin{figure} [h]
    \centering
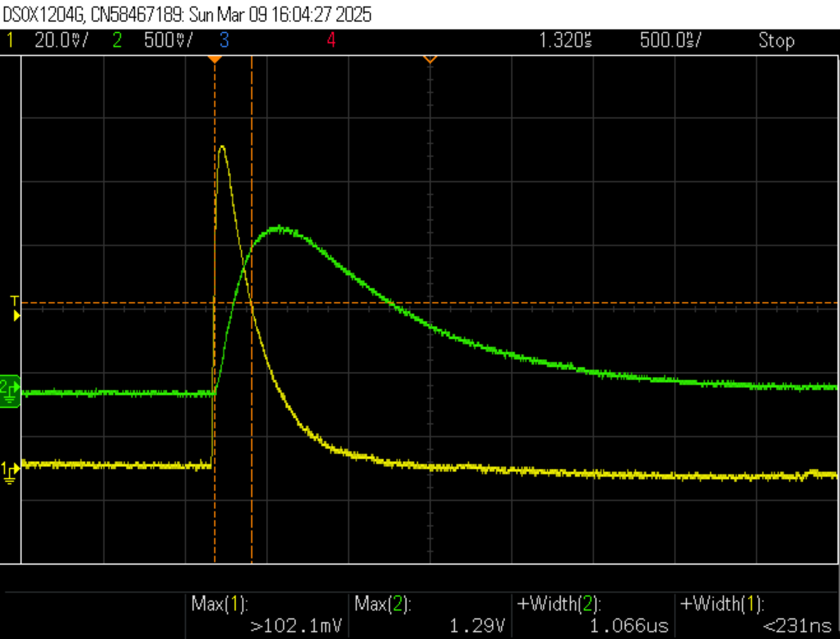
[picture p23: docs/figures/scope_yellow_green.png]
    
    \caption{Initial amplification testing with OnSemi C-Series SiPM (41\% photon detection efficiency (PDE), 420\,nm peak wavelength). \textbf{Yellow:} voltage across $49.9\,\Omega \pm 1\%$ shunt resistor on reverse-biased diode anode. \textbf{Green:} non-inverting op-amp configuration (LT1807) output. Light output measured from BC408 PVT scintillator.
}
    \label{fig3}
\end{figure}

%oscilloscope 2
\begin{figure} [h]
    \centering
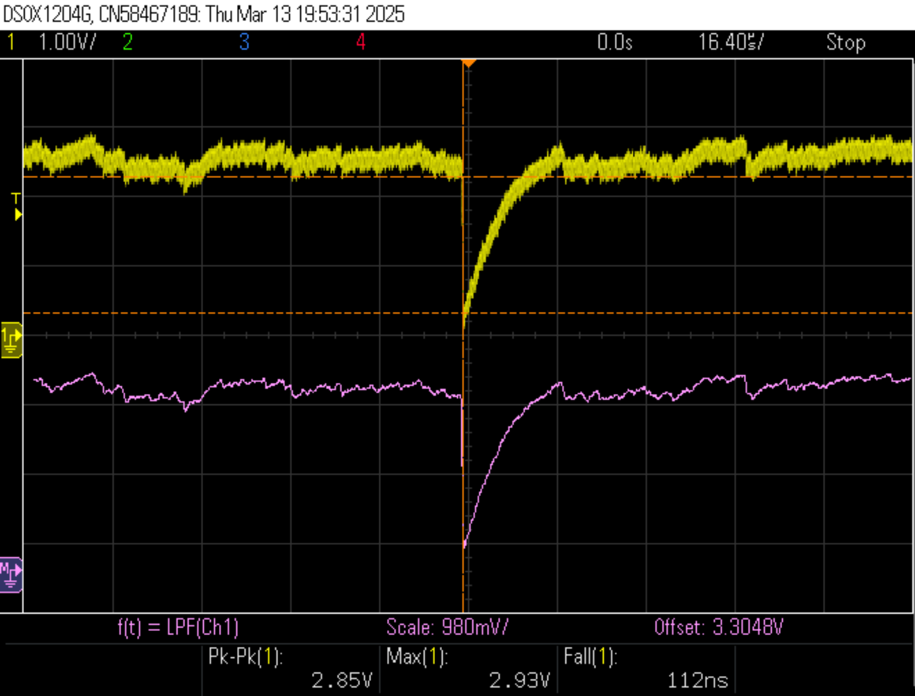
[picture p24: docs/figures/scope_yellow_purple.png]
    
    \caption{Initial transimpedance amplifier testing. Gain of $2.26 \times 10^5 \pm 1\%$. \textbf{Yellow:} inverting op-amp output. \textbf{Pink:} low-pass filter, 940\,kHz bandwidth.}
    \label{fig4}
\end{figure}

%Angle model
\begin{figure} [h]
    \centering
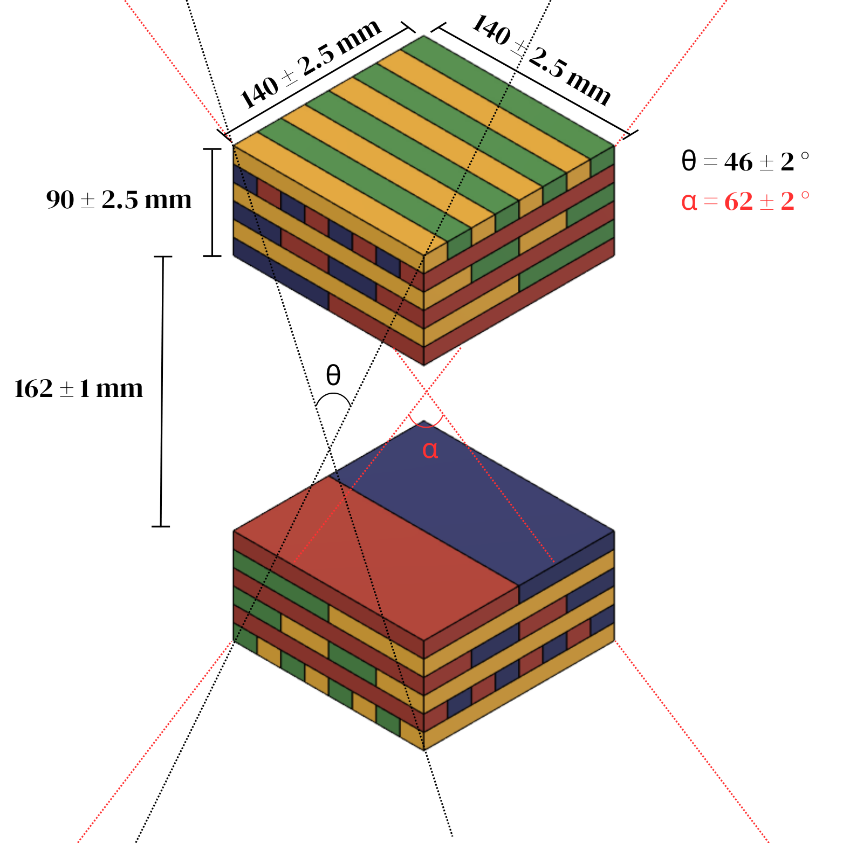
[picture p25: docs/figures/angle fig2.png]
    
    \caption{Cosmic ray capturing field of view: $46\pm2\degree$ minimum (on X and Y axes side projection), $62\pm2\degree$ maximum (on diagonal). Top and bottom scintillator stacks are $140\times140\times90 \pm2.5$ mm\textemdash separated by an air-gap of $162 \pm1$ mm. The minimum trajectory volume cross-section is $15\times15\text{ mm}: 225\text{ mm}^2$.}
    \label{angles}
\end{figure}

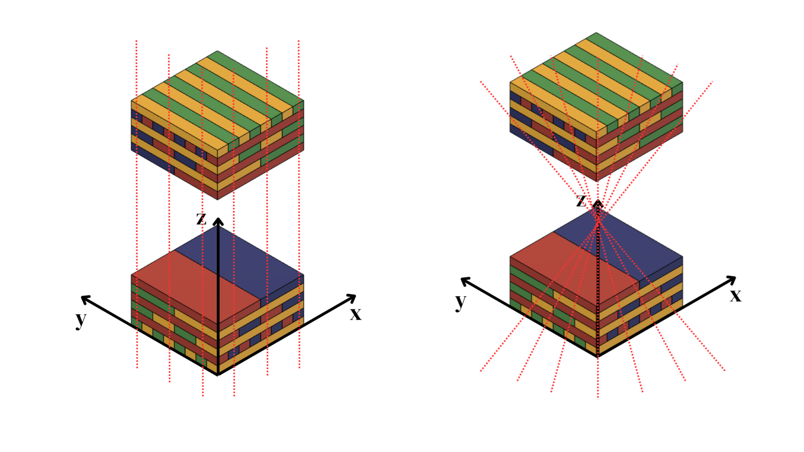
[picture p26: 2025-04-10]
docs/figures/test_proposal.png

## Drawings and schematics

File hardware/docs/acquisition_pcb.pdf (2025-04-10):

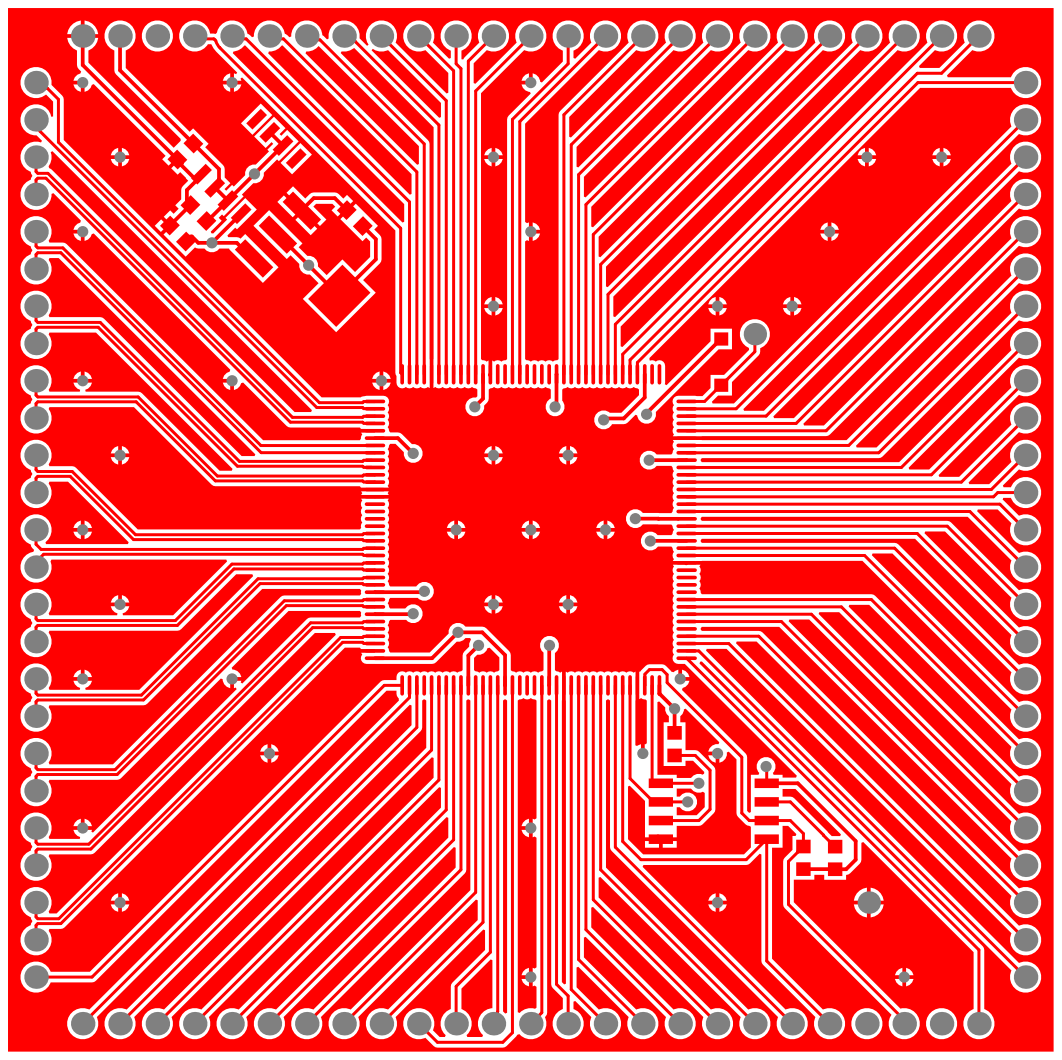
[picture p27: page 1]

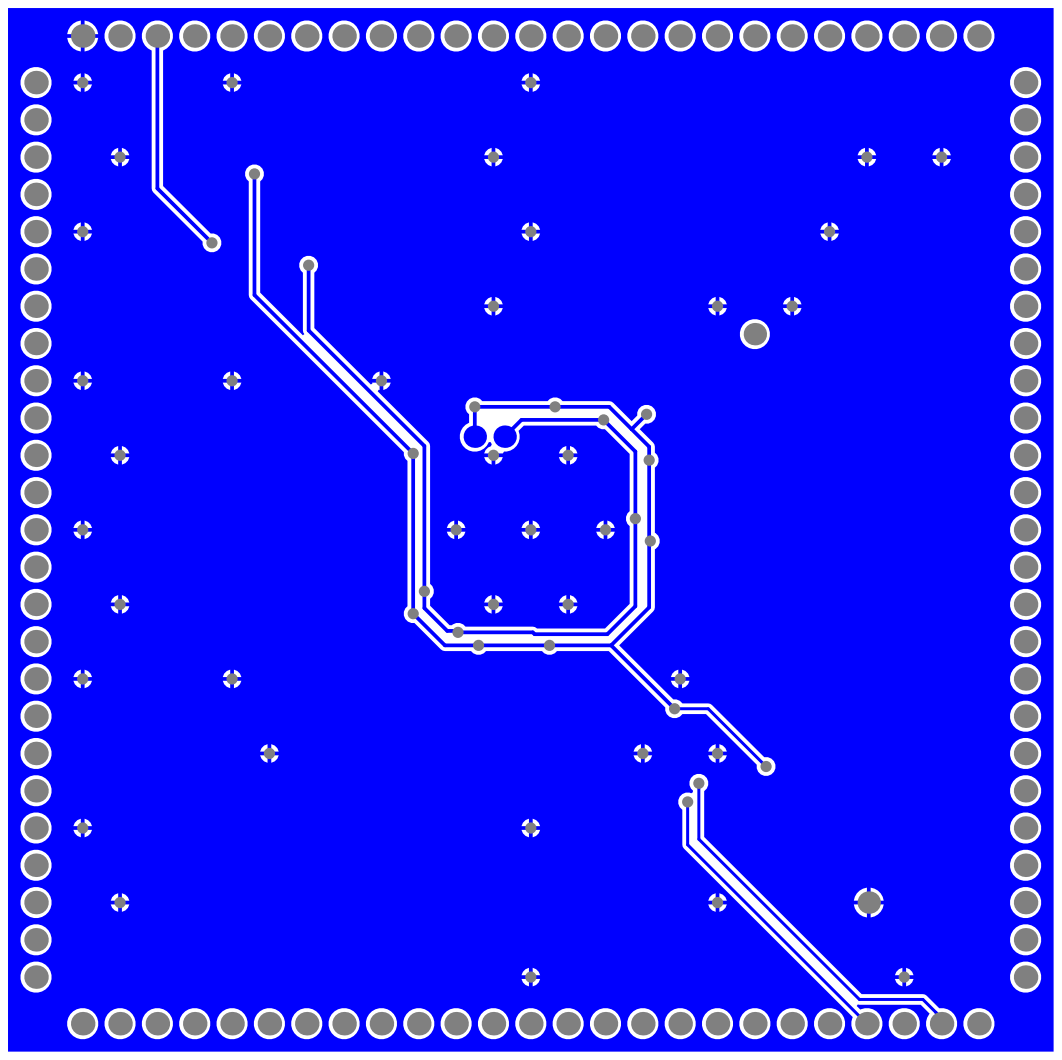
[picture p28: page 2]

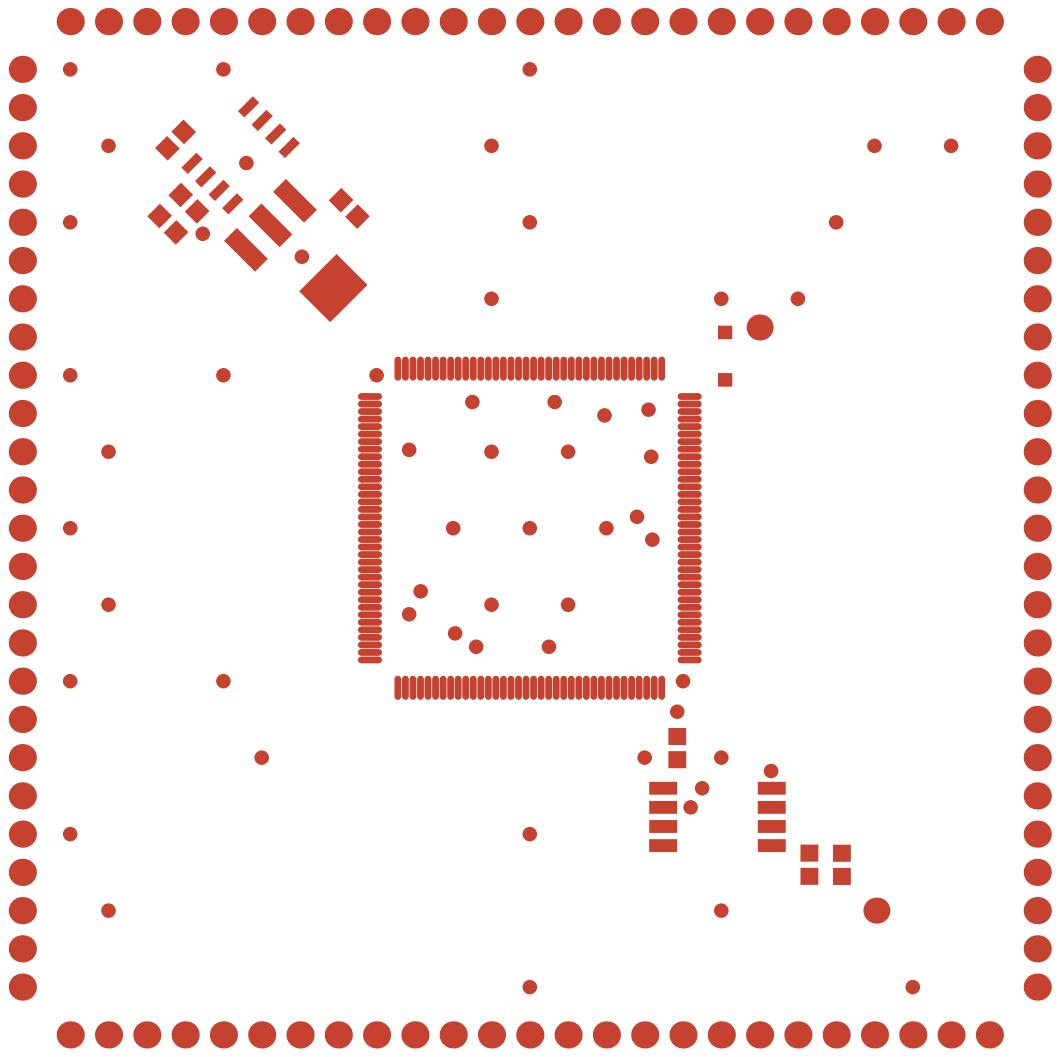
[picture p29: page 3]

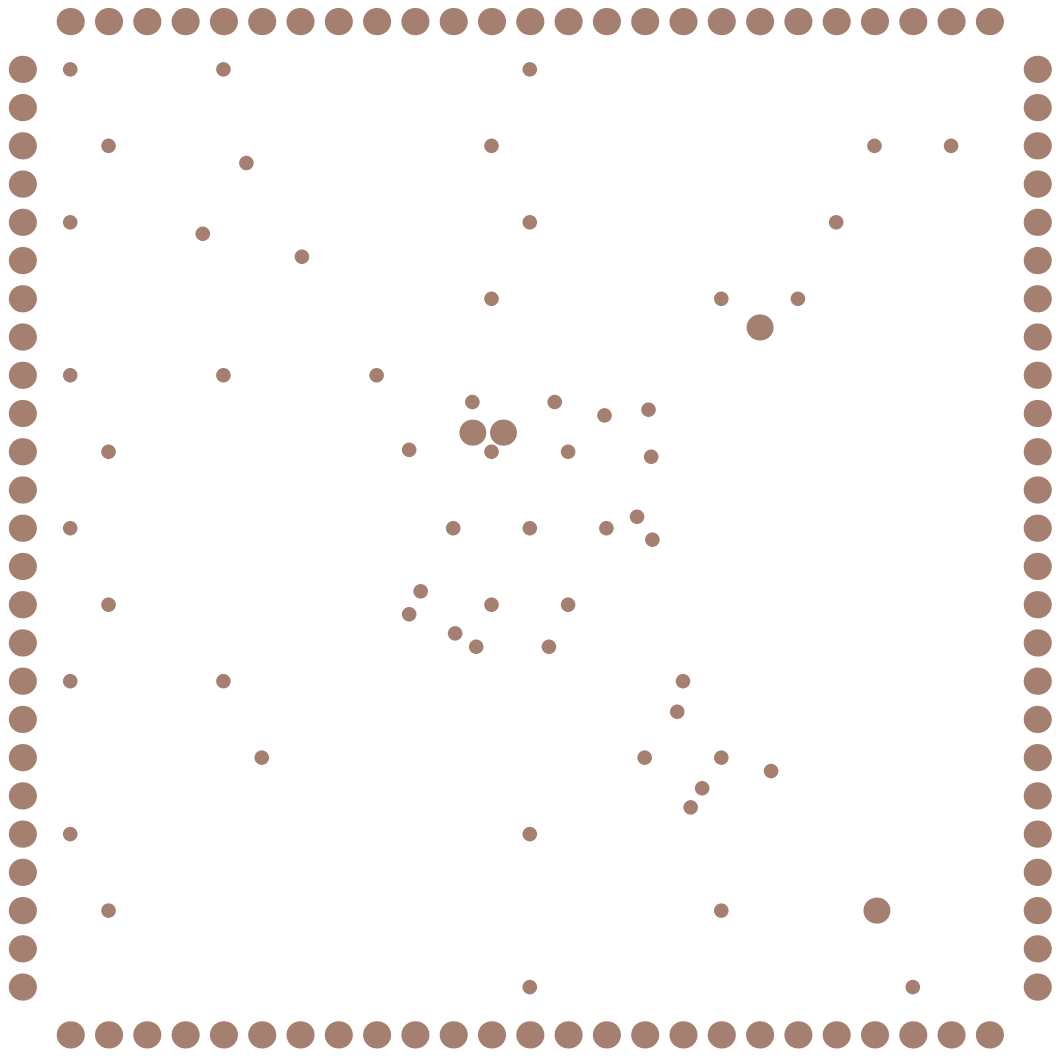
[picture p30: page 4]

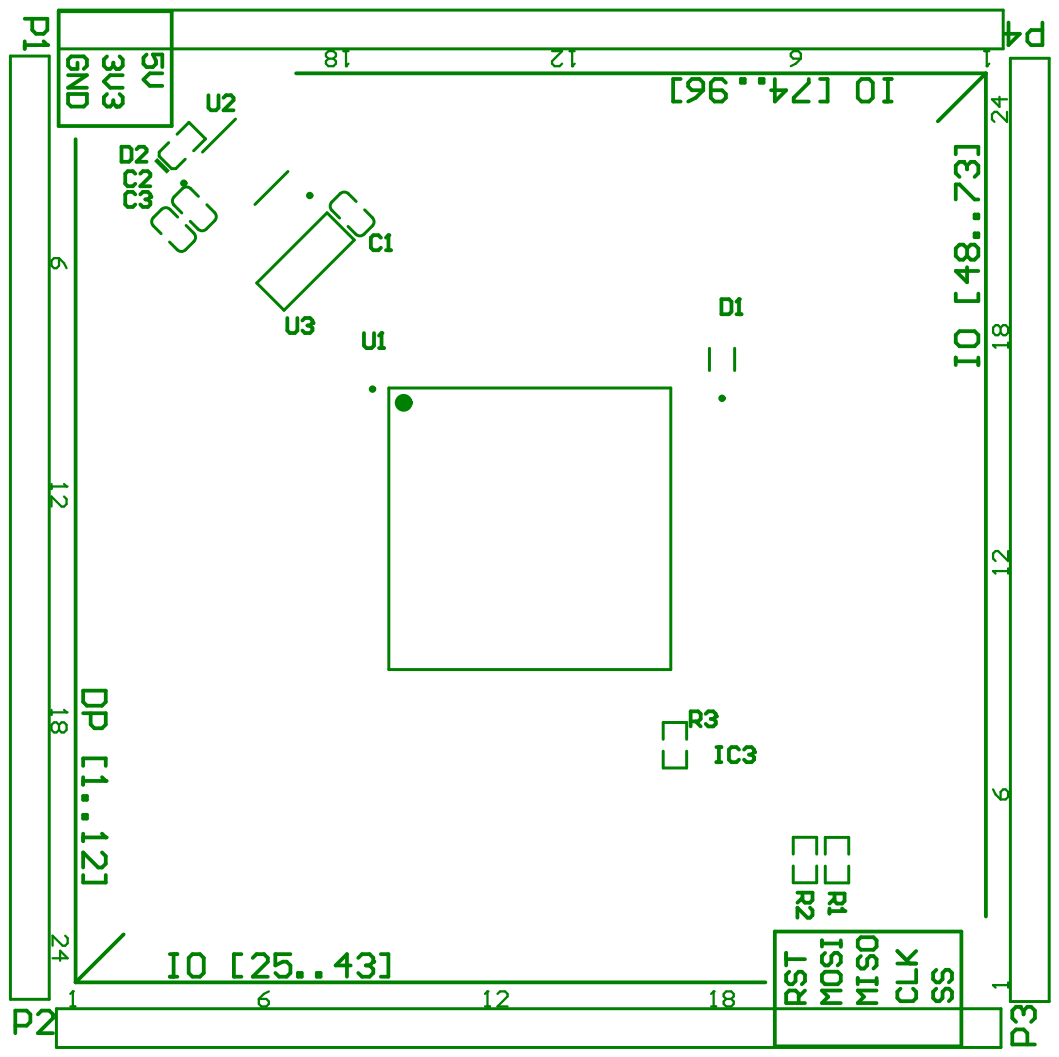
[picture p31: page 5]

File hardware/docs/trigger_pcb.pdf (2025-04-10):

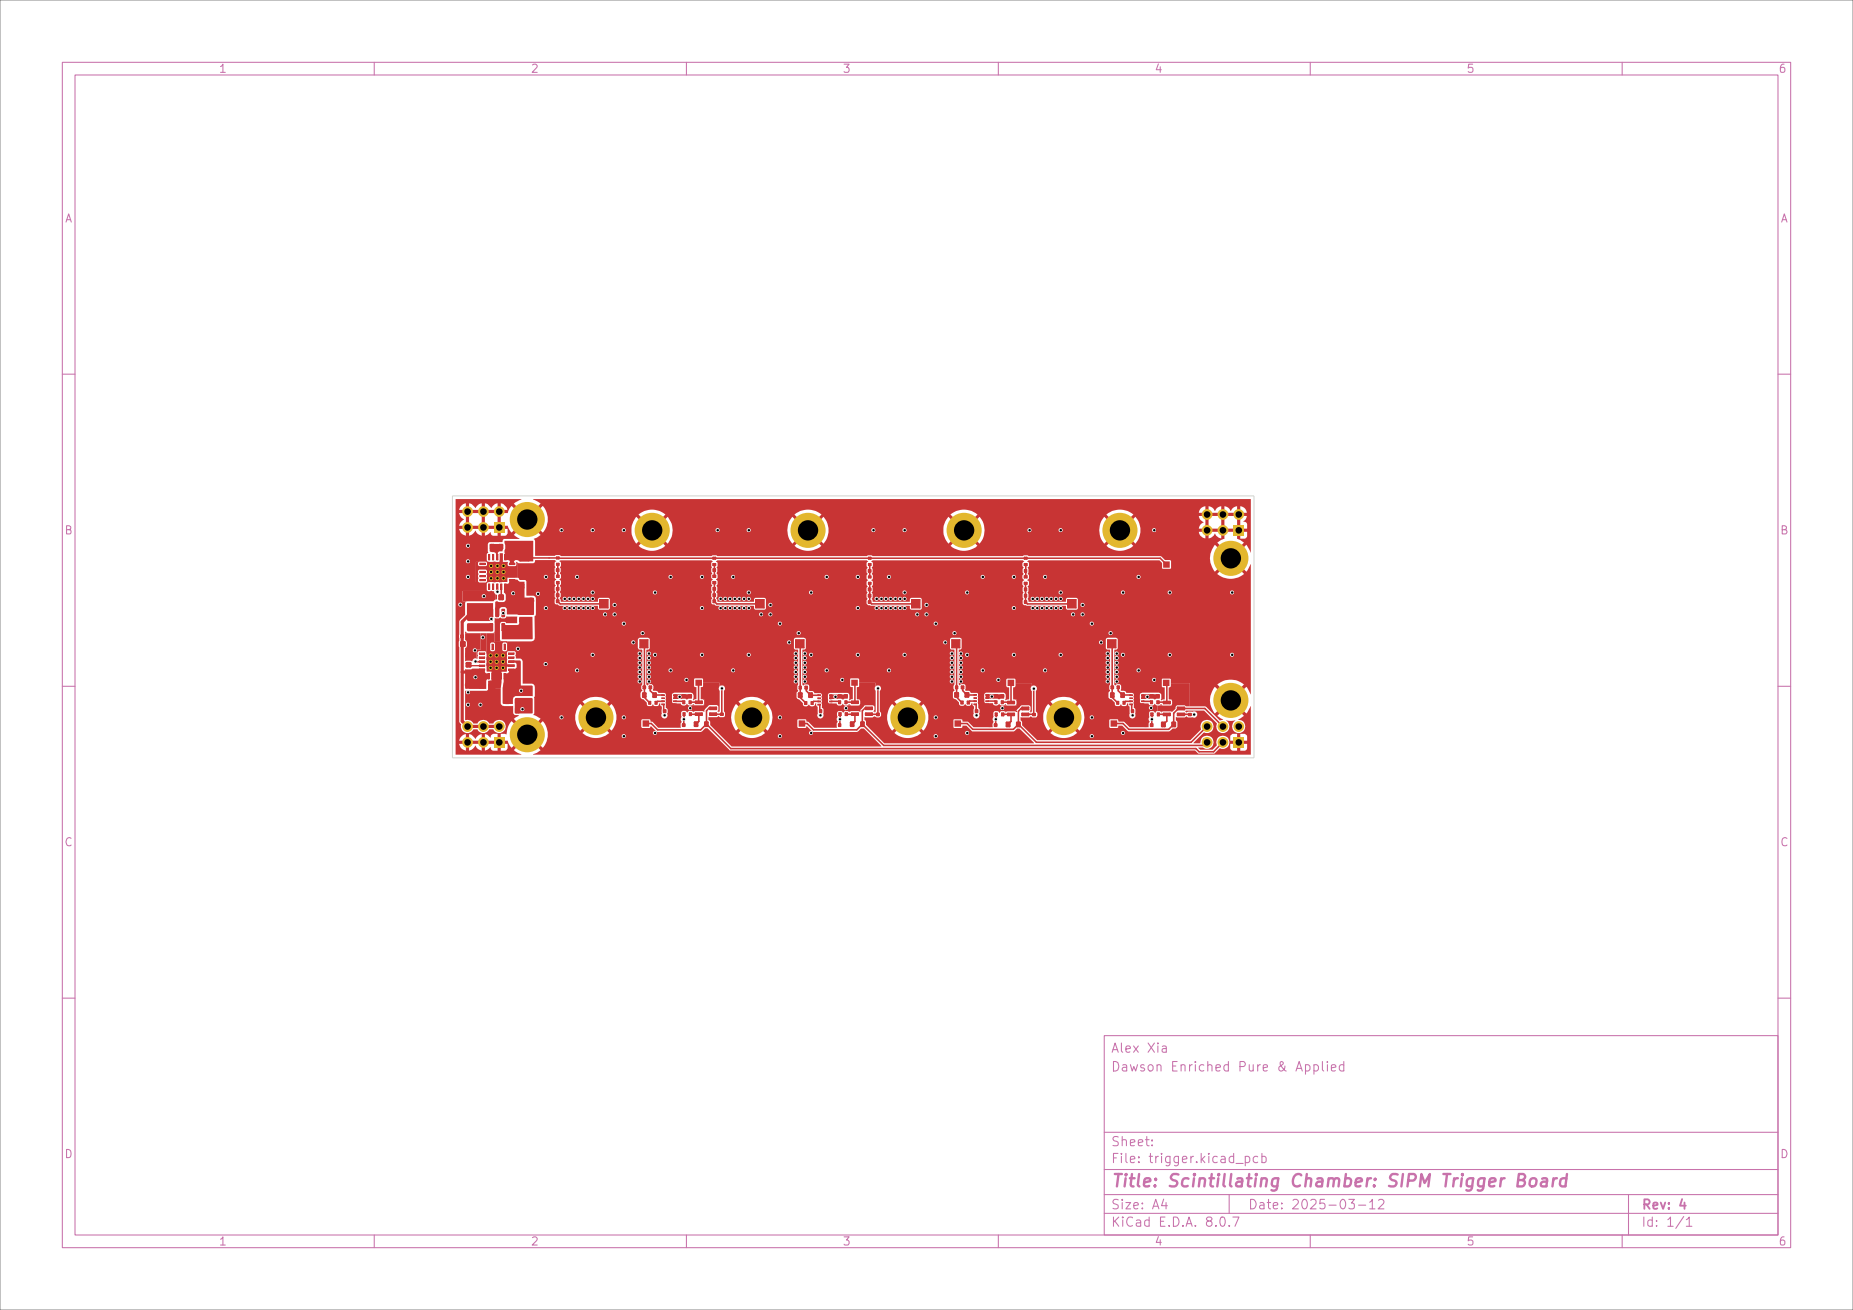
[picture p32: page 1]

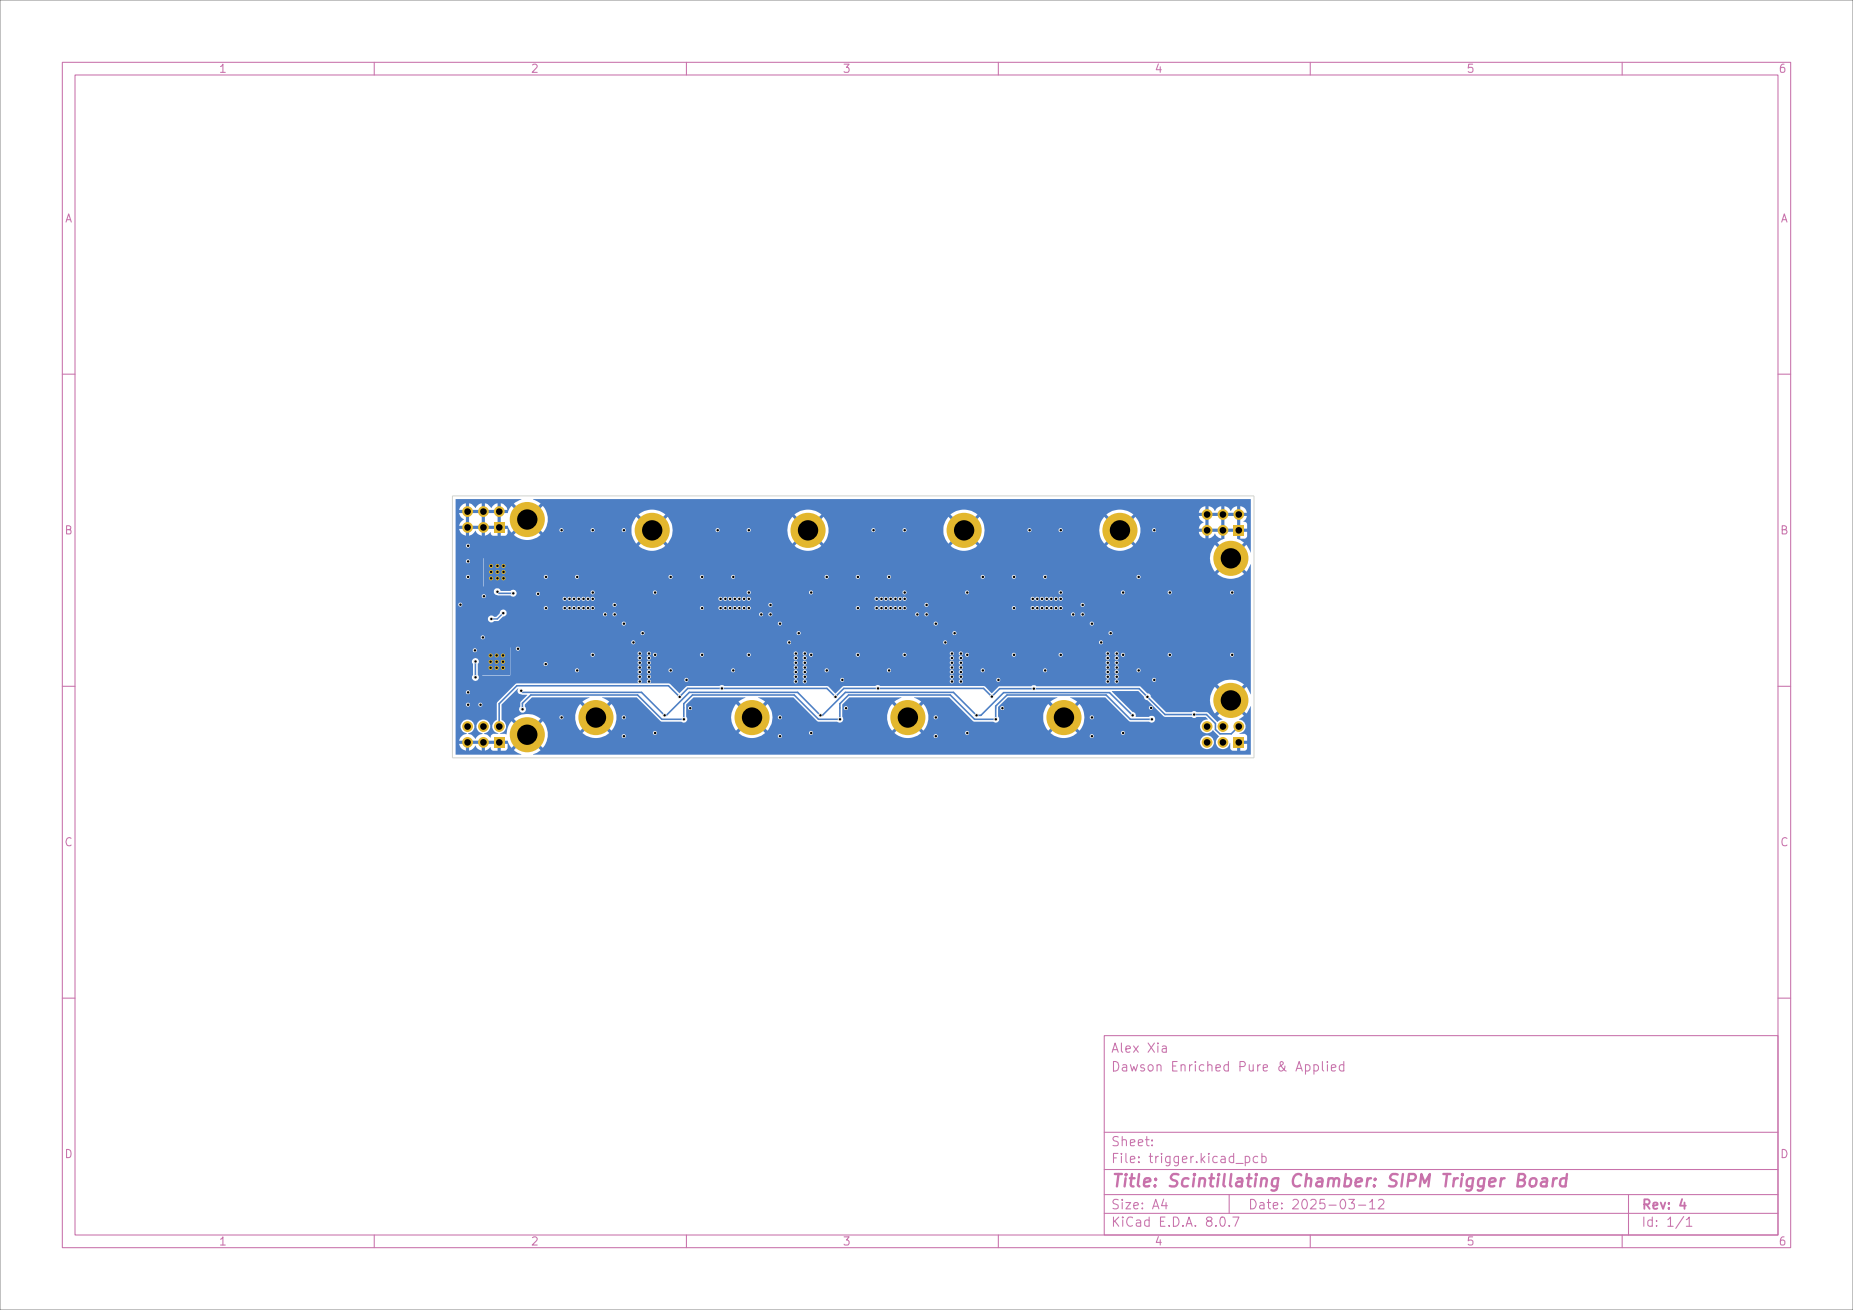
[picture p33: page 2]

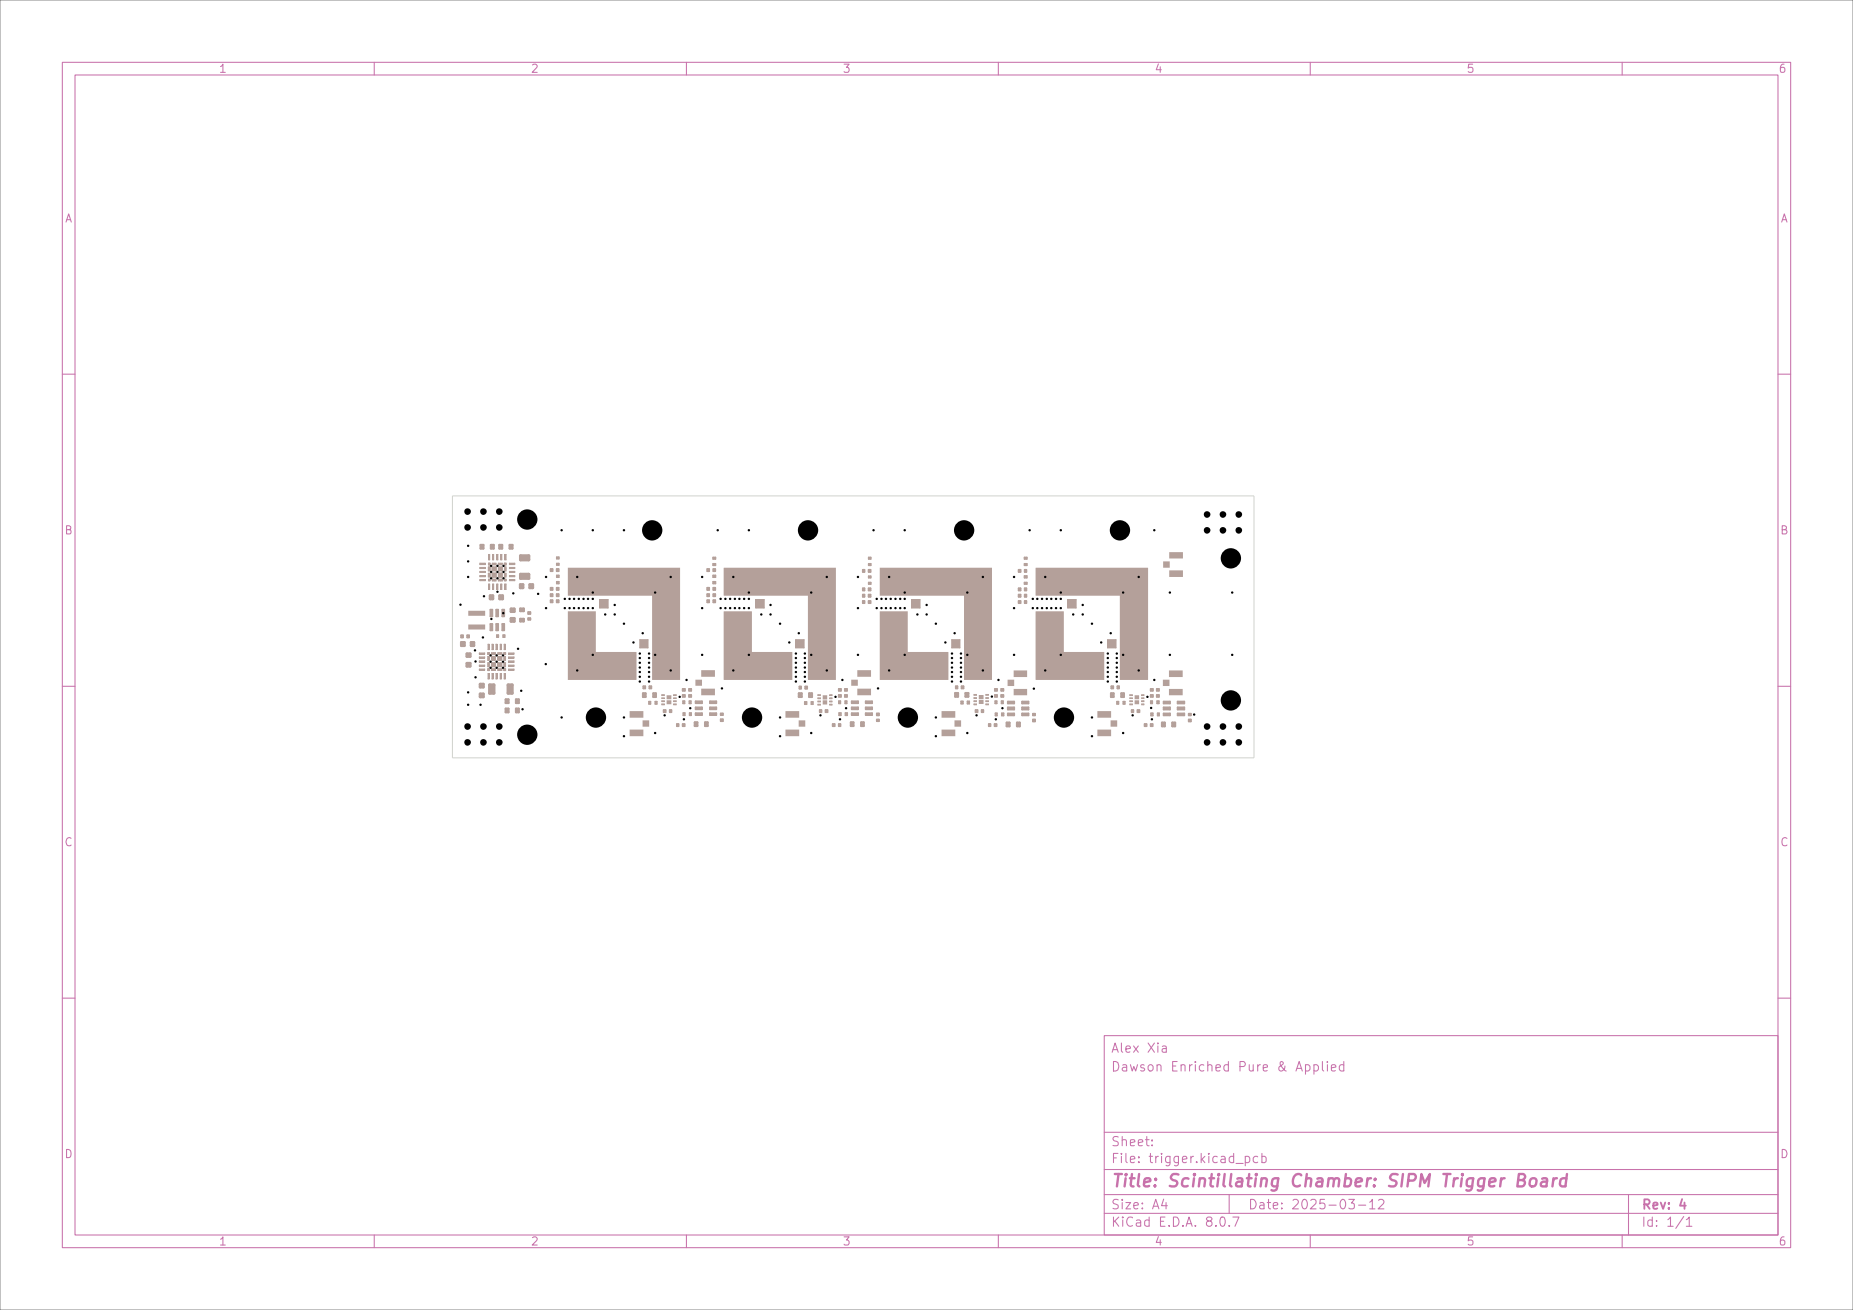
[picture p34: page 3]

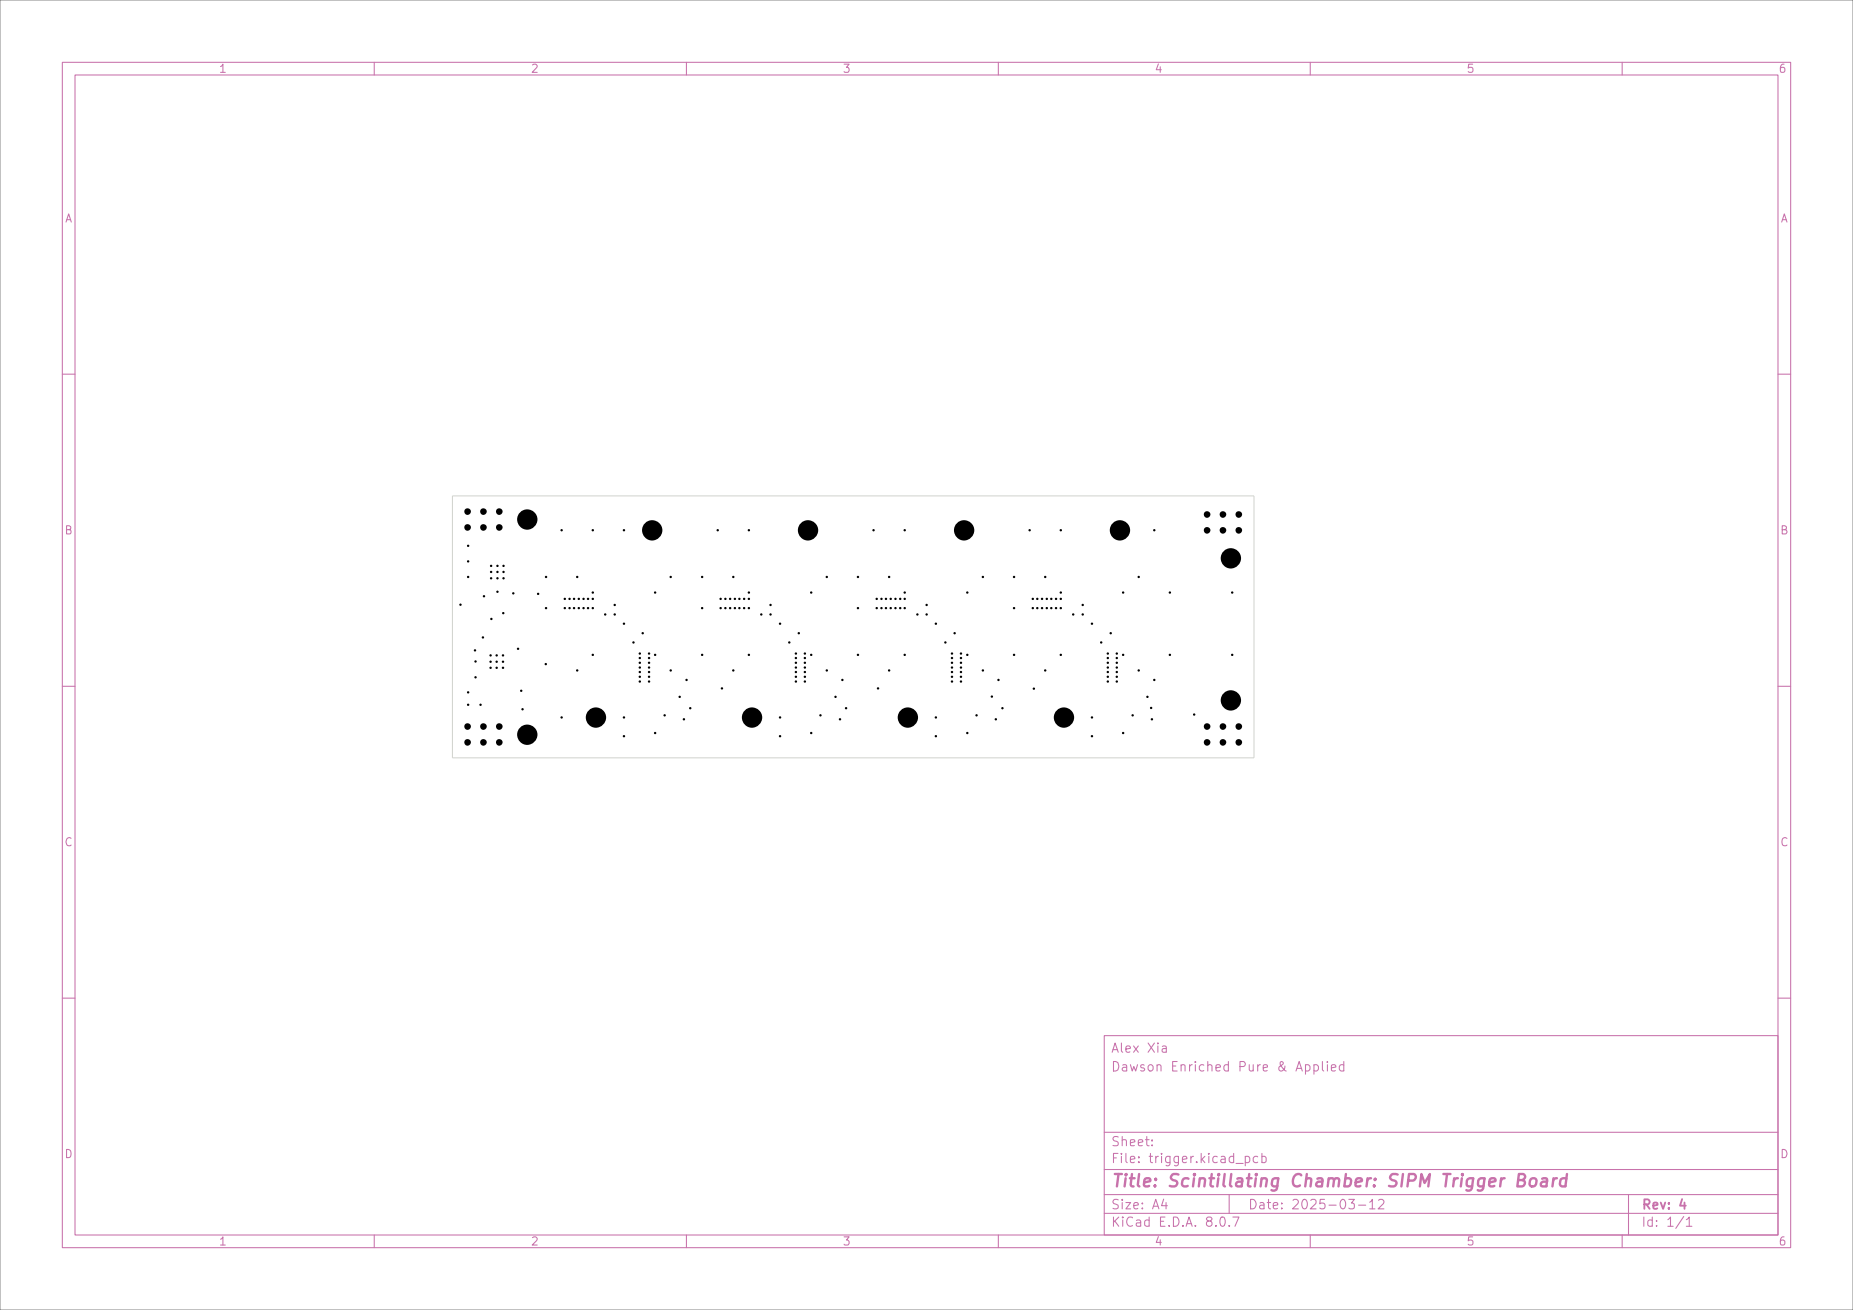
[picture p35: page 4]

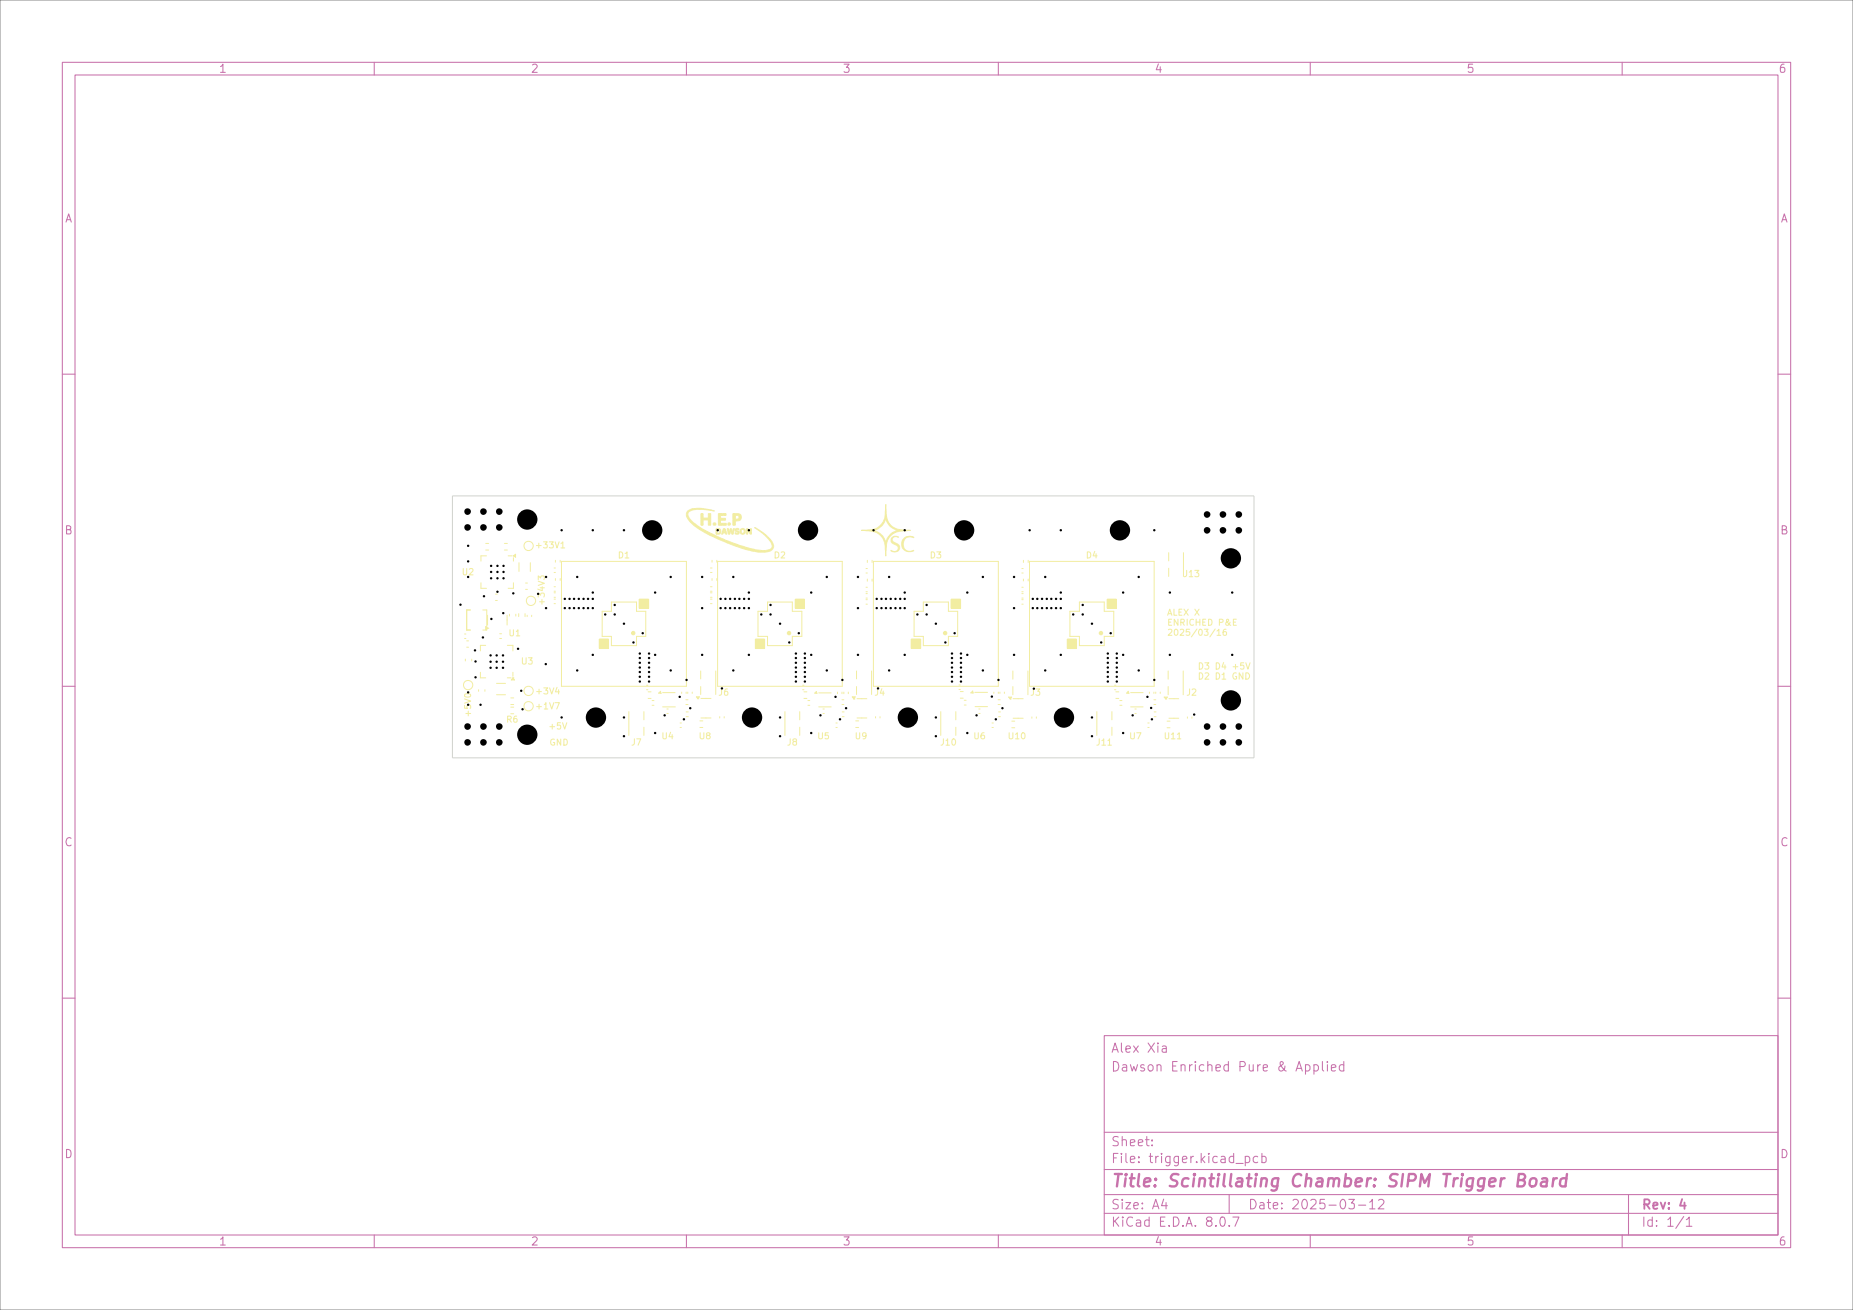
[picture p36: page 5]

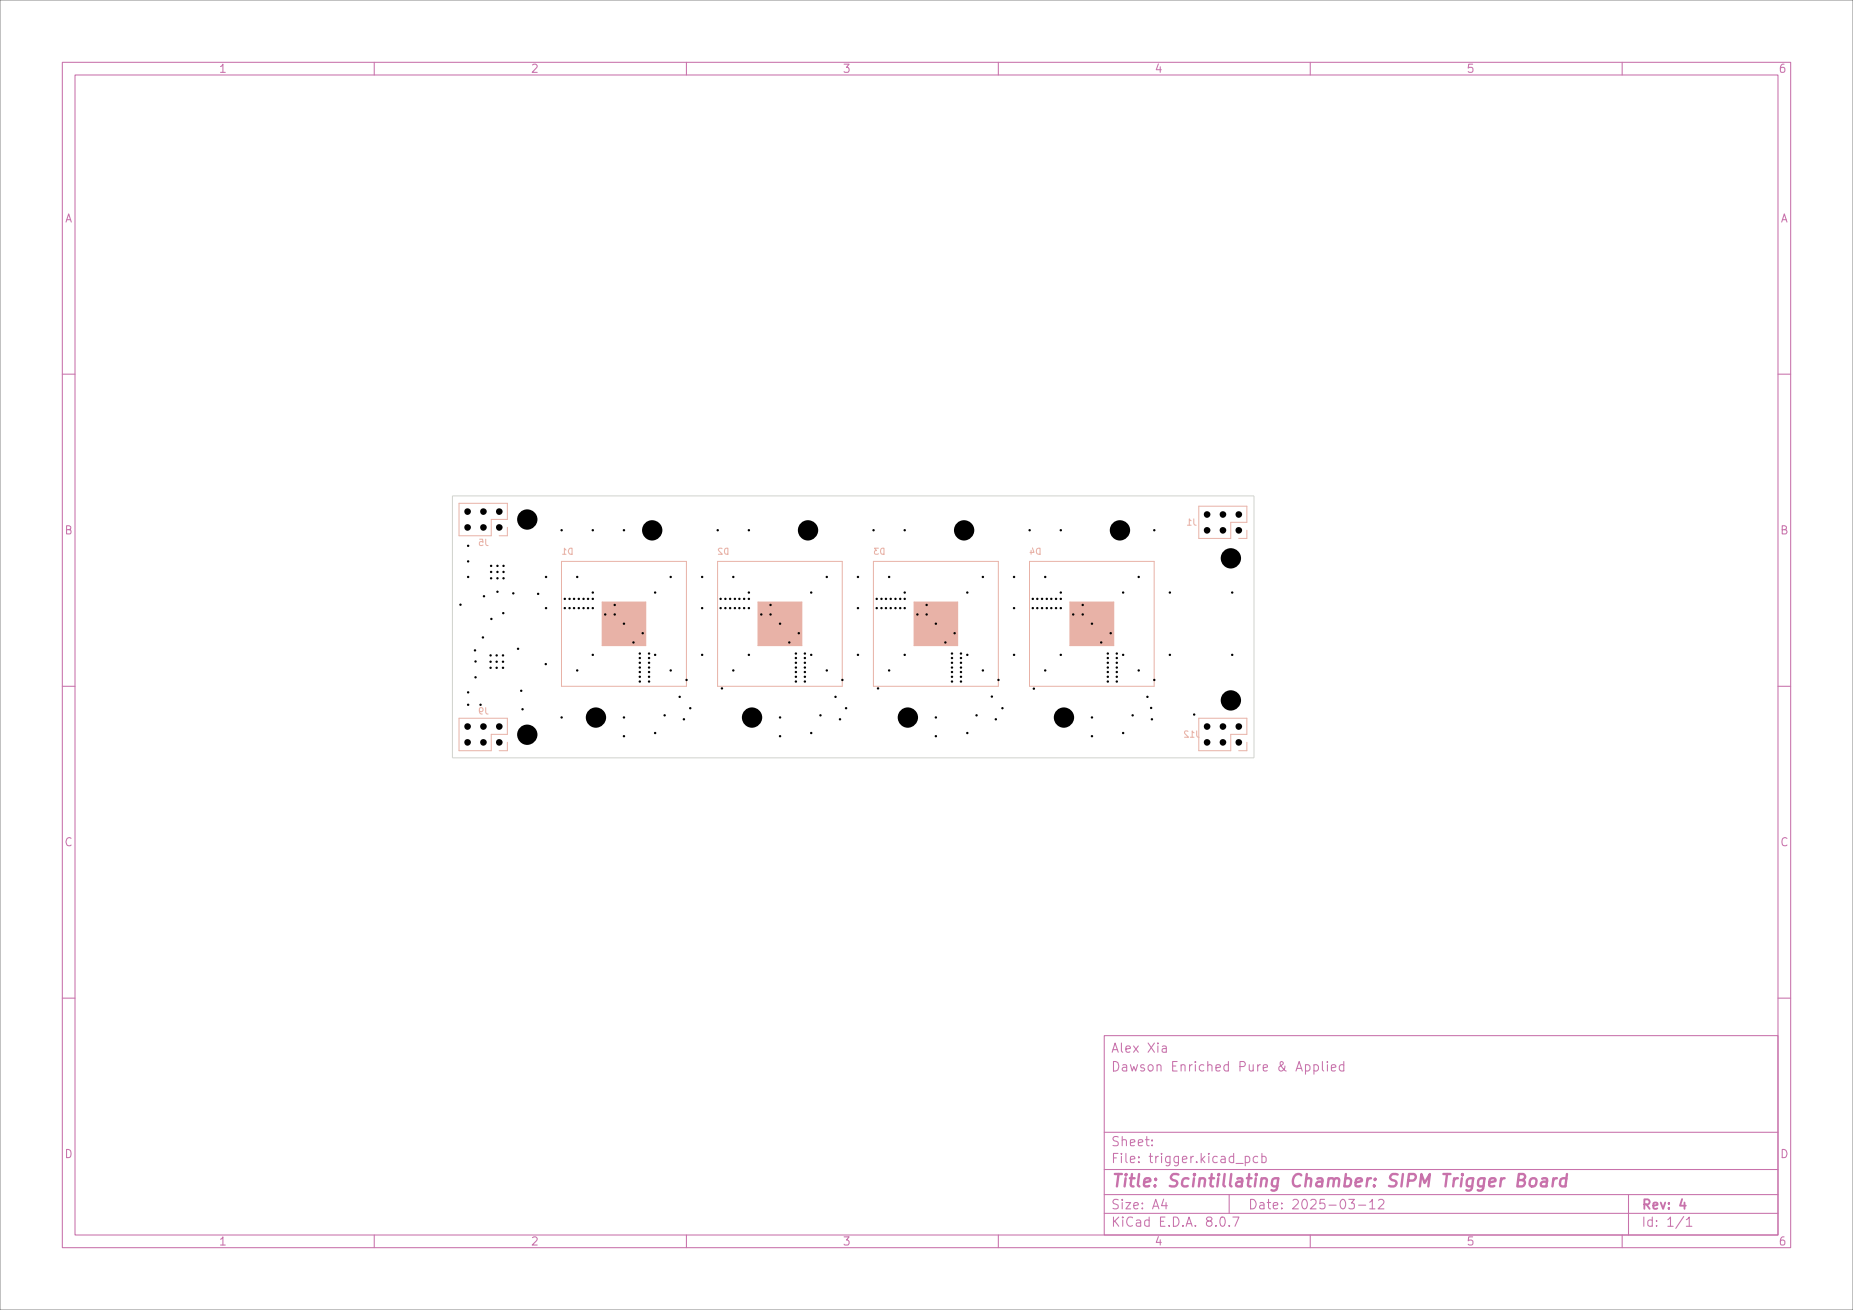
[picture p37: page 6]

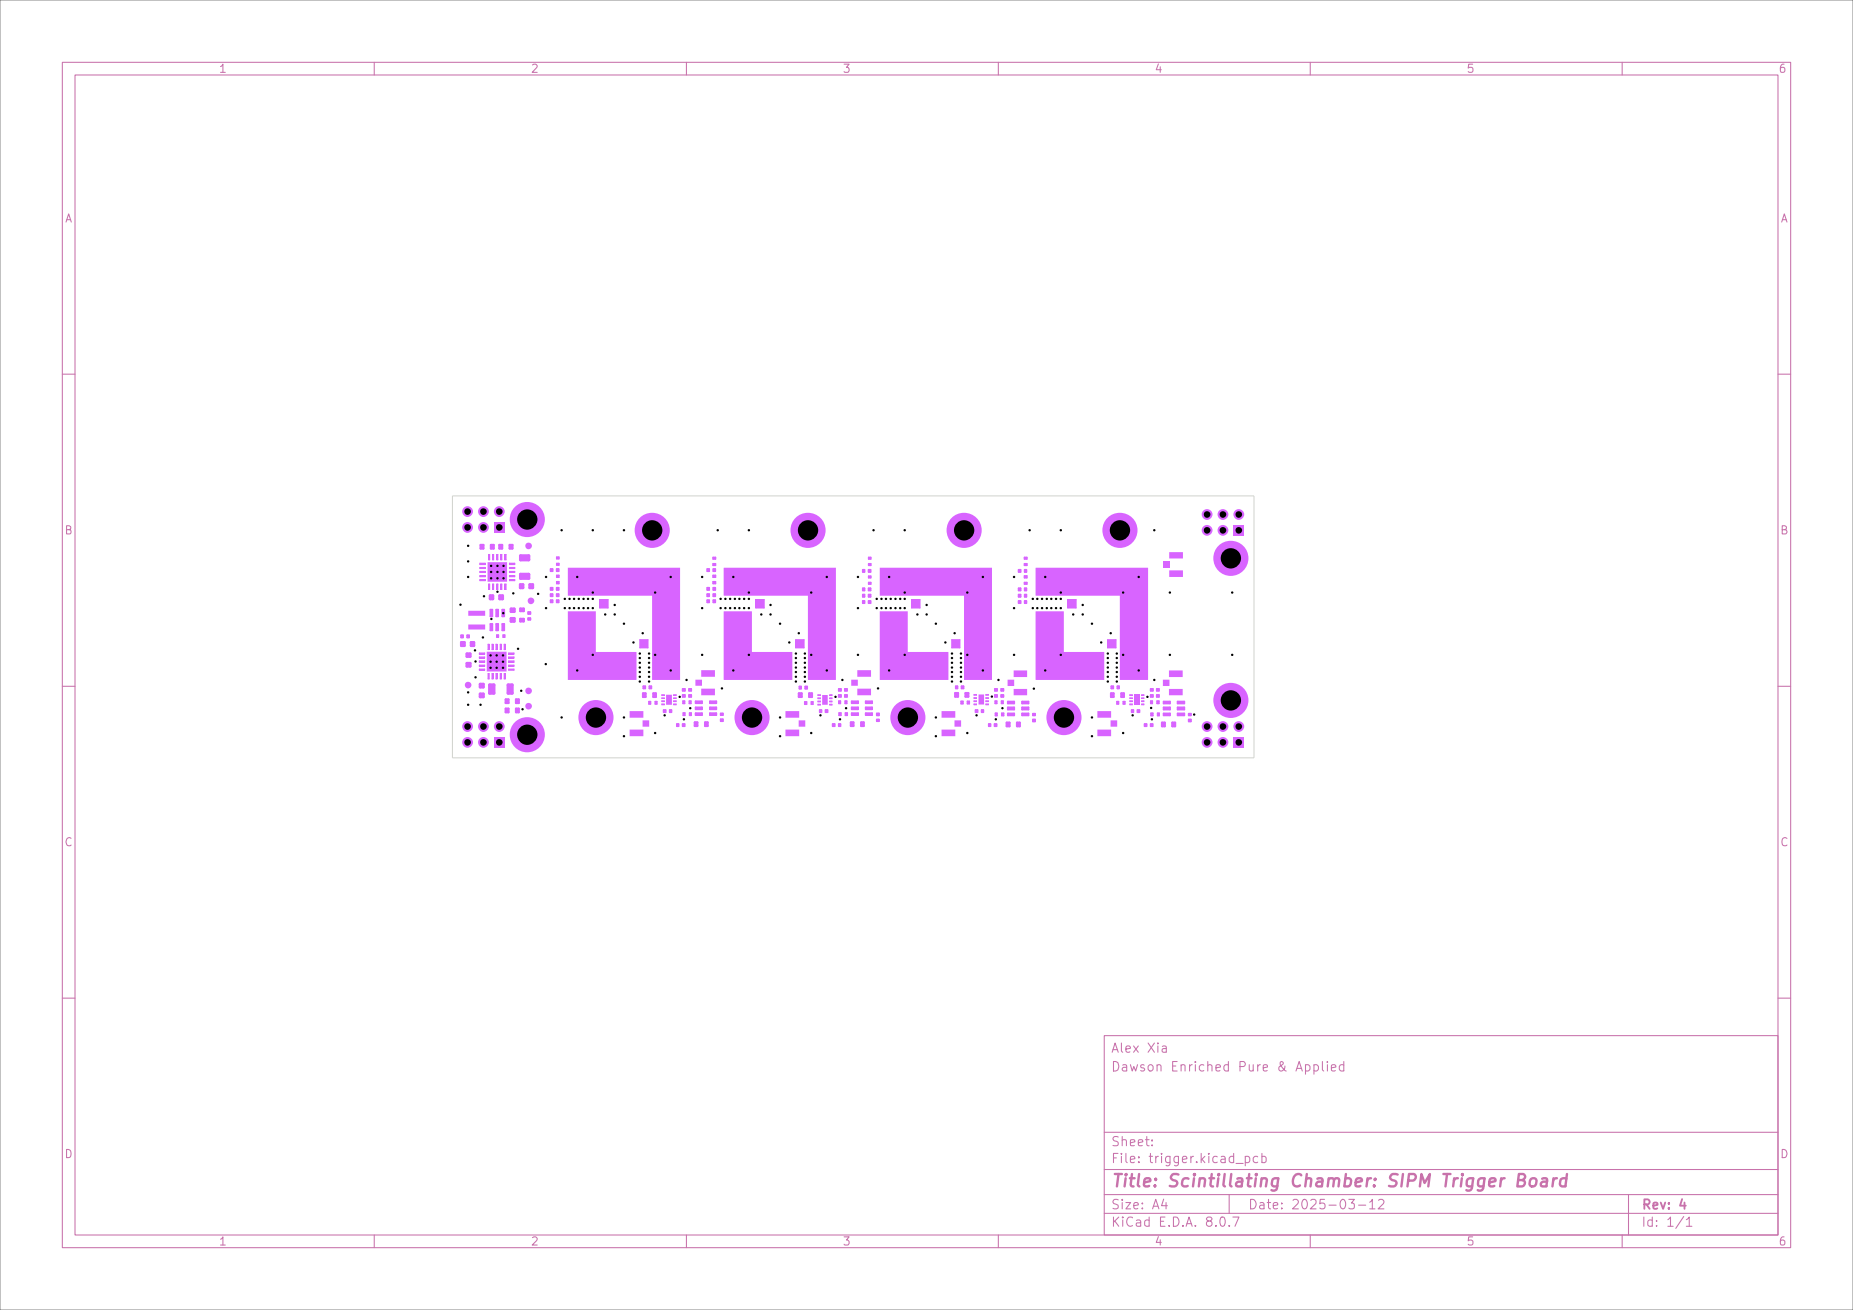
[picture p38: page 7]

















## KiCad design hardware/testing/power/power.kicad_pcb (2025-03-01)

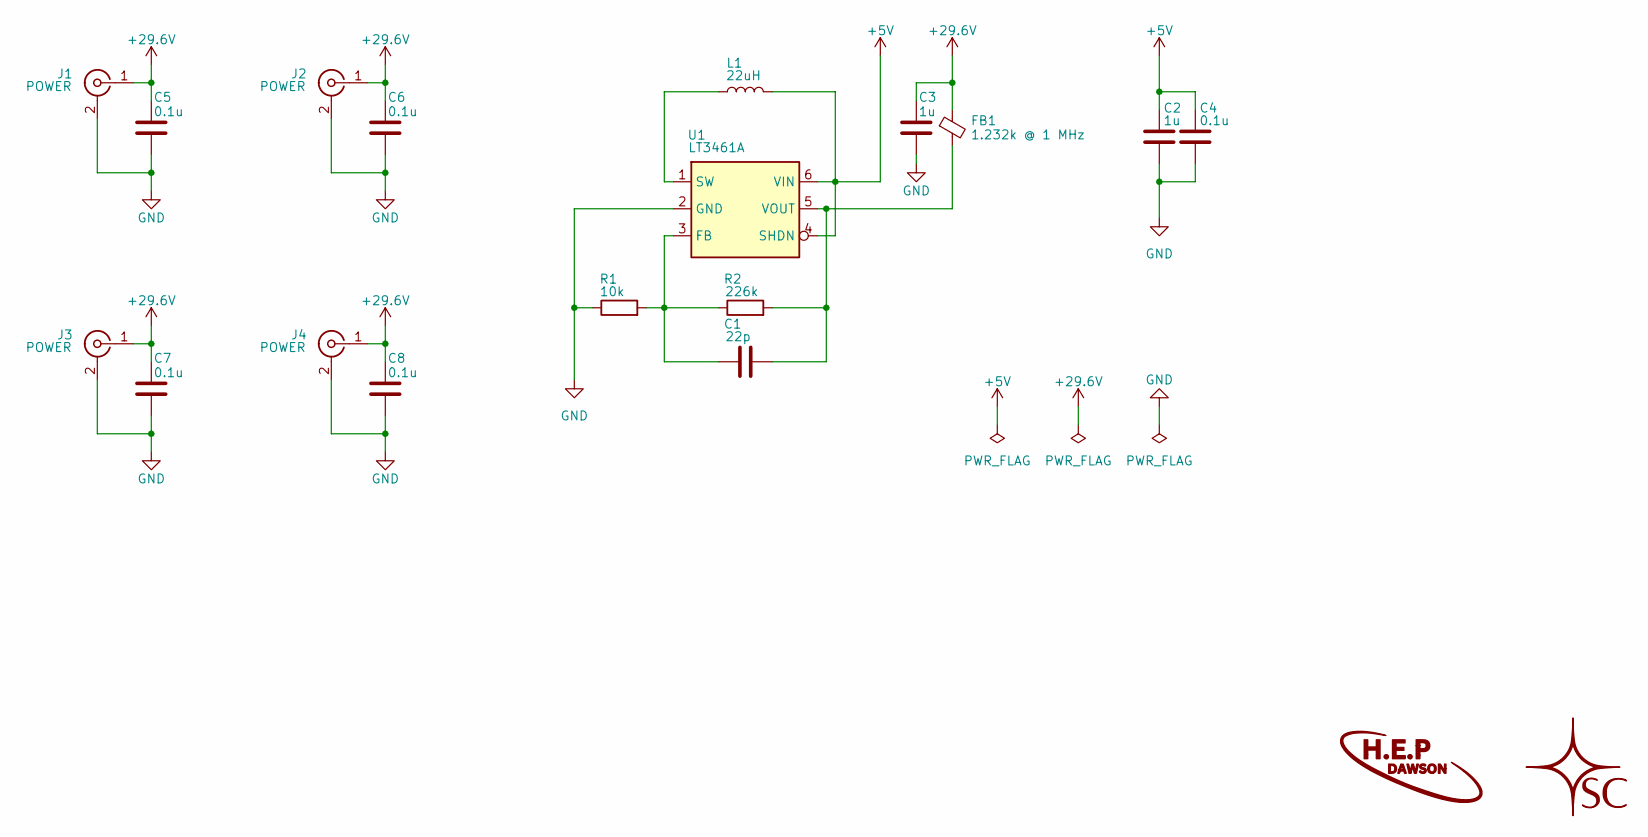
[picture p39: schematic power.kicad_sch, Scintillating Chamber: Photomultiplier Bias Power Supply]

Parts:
C1: 22p; C_0805_2012Metric_Pad1.18x1.45mm_HandSolder
C2, C3: 1u; C_0805_2012Metric_Pad1.18x1.45mm_HandSolder
C4, C5, C6, C7, C8: 0.1u; C_0805_2012Metric_Pad1.18x1.45mm_HandSolder
FB1: 1.232k @ 1 MHz; FB_TDK_VFS6045_2424_6060Metric_HandSoldering
J1, J2, J3, J4: POWER; SMA_Amphenol_901-144_Vertical
L1: 22uH; L_Laird_TYS3015_HandSoldering
R1: 10k; R_0805_2012Metric_Pad1.20x1.40mm_HandSolder
R2: 226k; R_0805_2012Metric_Pad1.20x1.40mm_HandSolder
U1: LT3461A; TSOT-23-6_HandSoldering

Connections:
+5V: C2.1, C4.1, L1.2, U1.4 (SHDN), U1.6 (VIN)
+29.6V: C3.1, C5.1, C6.1, C7.1, C8.1, FB1.1, J1.1 (In), J2.1 (In), J3.1 (In), J4.1 (In)
GND: C2.2, C3.2, C4.2, C5.2, C6.2, C7.2, C8.2, J1.2 (Ext), J2.2 (Ext), J3.2 (Ext), J4.2 (Ext), R1.1, U1.2 (GND)
unnamed: C1.1, R1.2, R2.1, U1.3 (FB)
unnamed: L1.1, U1.1 (SW)
unnamed: C1.2, FB1.2, R2.2, U1.5 (VOUT)

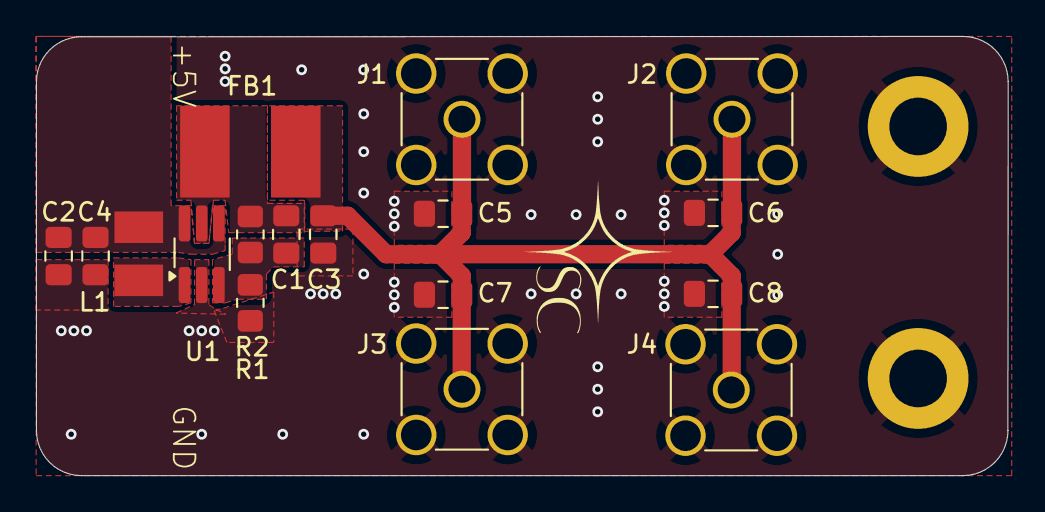
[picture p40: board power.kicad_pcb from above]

Board: 2 copper layers, 54.0 x 24.4 mm, 17 parts (0 on the bottom side), 6 nets.

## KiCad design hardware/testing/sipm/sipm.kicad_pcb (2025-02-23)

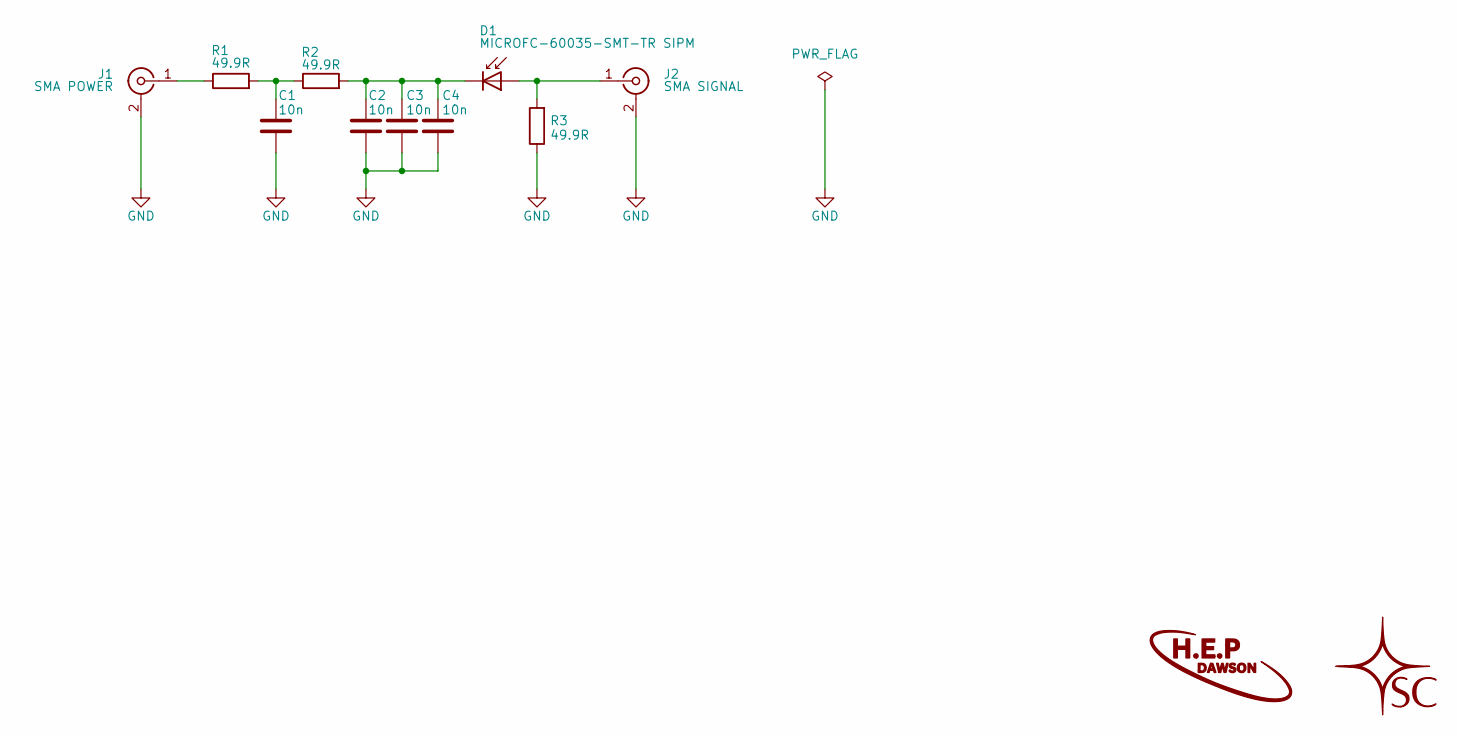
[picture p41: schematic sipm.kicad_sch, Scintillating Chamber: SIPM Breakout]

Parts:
C1, C2, C3, C4: 10n; C_0805_2012Metric_Pad1.18x1.45mm_HandSolder
D1: MICROFC-60035-SMT-TR SIPM; MICROFC-60035-SMT-TR
J1: SMA POWER; SMA_Amphenol_901-144_Vertical
J2: SMA SIGNAL; SMA_Amphenol_901-144_Vertical
R1, R2, R3: 49.9R; R_0805_2012Metric_Pad1.20x1.40mm_HandSolder

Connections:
GND: C1.2, C2.2, C3.2, C4.2, J1.2 (Ext), J2.2 (Ext), R3.1
unnamed: C1.1, R1.2, R2.1
unnamed: D1.2 (A), J2.1 (In), R3.2
unnamed: C2.1, C3.1, C4.1, D1.1 (K), R2.2
unnamed: J1.1 (In), R1.1

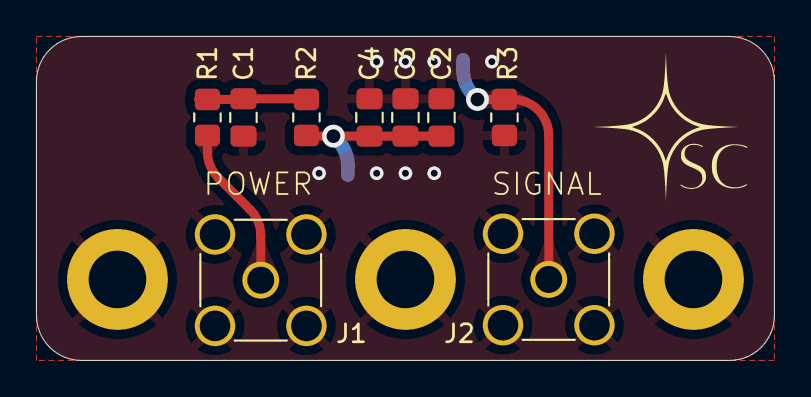
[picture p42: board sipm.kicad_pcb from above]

Board: 2 copper layers, 41.0 x 18.0 mm, 10 parts (1 on the bottom side), 5 nets.

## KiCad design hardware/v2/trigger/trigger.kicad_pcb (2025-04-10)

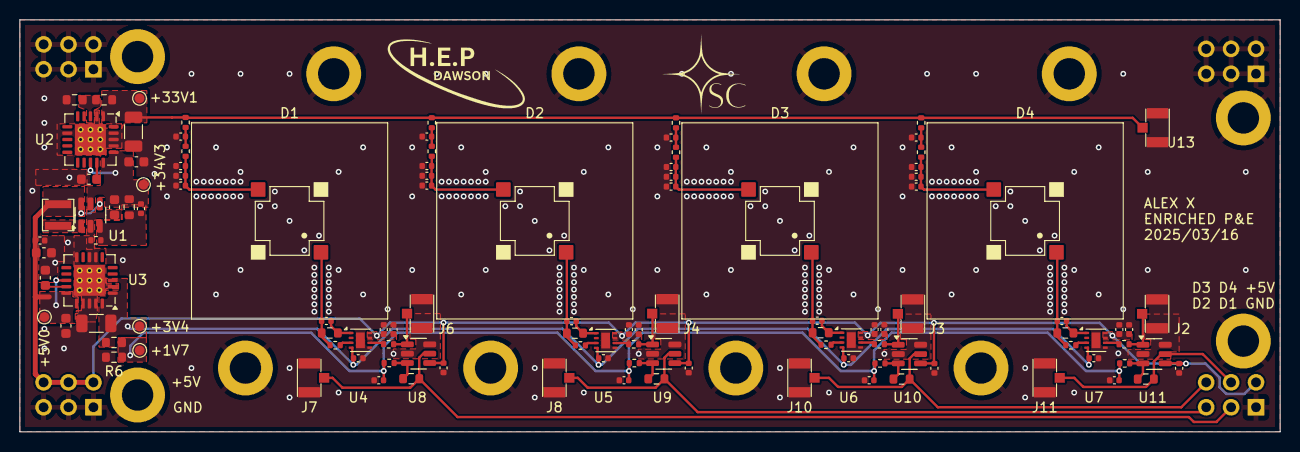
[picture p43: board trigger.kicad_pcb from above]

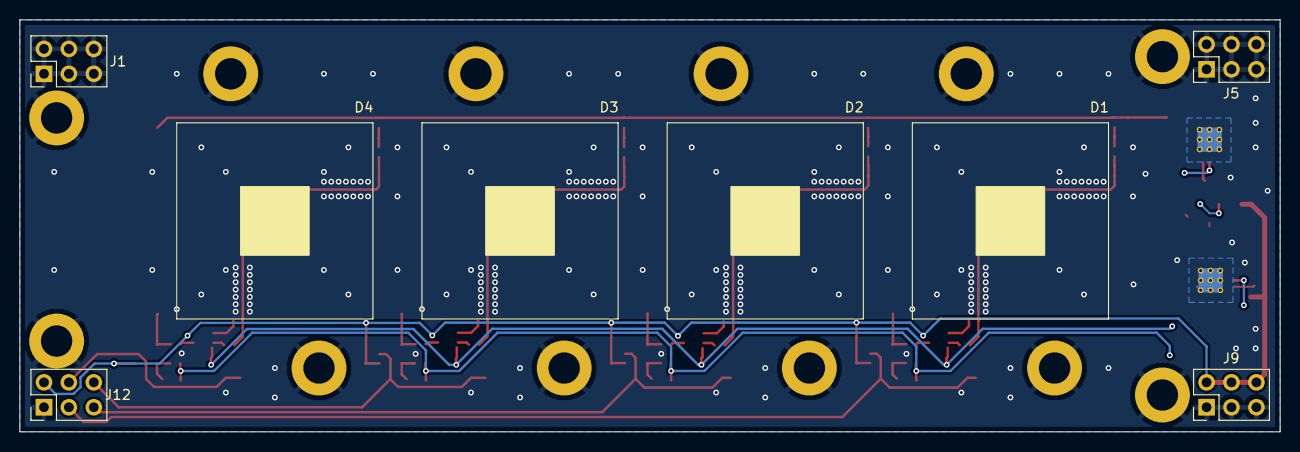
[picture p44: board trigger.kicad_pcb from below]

Board: 2 copper layers, 128.5 x 42.0 mm, 130 parts (4 on the bottom side), 47 nets.

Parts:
+1V7, +3V4, +5V0, +33V1, +34V3: TestPoint; TestPoint_Pad_D1.0mm
C1: 22p; C_0402_1005Metric
C2, C31, C32, C33, C34, C41, C42, C43, C44: 0.1u; C_0402_1005Metric
C3, C4, C5, C6, C8, C9: 1u; C_0603_1608Metric
C7, C10: 10u; C_1206_3216Metric
C11, C12, C13, C14, C15, C16, C17, C18, C19, C20, C21, C22, C23, C24, C25, C26, C37, C38, C39, C40, C47, C48, C49, C50: 10n; C_0402_1005Metric
C27, C28, C29, C30: 3p; C_0402_1005Metric
C35, C36, C45, C46: 2.2u; C_0402_1005Metric
D1, D2, D3, D4: MICROFC-60035-SMT-TR SIPM; MICROFC-60035-SMT-TR
H1, H2, H3, H4, H5, H6, H7, H8, H9, H10, H11, H12: M3; MountingHole_3.2mm_M3_DIN965_Pad
J1, J5, J9, J12: Conn_02x03_Top_Bottom; PinHeader_2x03_P2.54mm_Vertical
J2, J3, J4, J6, J7, J8, J10, J11, J13: Conn_Coaxial_Small; BWIPX-1-001E
L1: 22u; L_Murata_LQH3NPN_3.0x3.0mm
R1: 12k 0.1%; R_0402_1005Metric
R2: 316k 0.1%; R_0603_1608Metric
R3, R19, R20, R21, R22: 226k 0.1%; R_0603_1608Metric
R4, R5, R6, R31, R32, R33, R34: 10k 0.1%; R_0603_1608Metric
R7, R8, R9, R10, R11, R12, R13, R14, R27, R28, R29, R30: 49.9R; R_0402_1005Metric
R15, R16, R17, R18: 20R; R_0402_1005Metric
R23, R24, R25, R26: 0; R_0402_1005Metric
U1: LT3461A; TSOT-23-6
U2, U3: TPS7A4701; Texas_RGW0020A_VQFN-20-1EP_5x5mm_P0.65mm_EP3.15x3.15mm_Ther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
U4, U5, U6, U7: OPA858xDSG; WSON-8-1EP_2x2mm_P0.5mm_EP0.9x1.6mm
U8, U9, U10, U11: TLV3501AIDBV; SOT-23-6

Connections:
+1.7V: +1V7.1, C37.1, C38.1, C47.1, C48.1, R5.2, R6.1, R27.2, R28.2, R29.2, R30.2
+3.4V: +3V4.1, C10.1, C39.1, C40.1, C49.1, C50.1, R5.1, U3.1 (OUT), U3.3 (SENSE/FB), U3.20 (OUT), U4.4 (+), U5.4 (+), U6.4 (+), U7.4 (+)
+5V: +5V0.1, C2.1, C3.1, C8.1, C31.1, C32.1, C33.1, C34.1, C35.1, C36.1, C41.1, C42.1, C43.1, C44.1, C45.1, C46.1, J9.4, J9.5, J9.6, J12.4, L1.2, U1.4 (SHDN), U1.6 (VIN), U3.13 (EN), U3.15 (IN), U3.16 (IN), U4.7 (V+), U4.8 (~PD), U5.7 (V+), U5.8 (~PD), U6.7 (V+), U6.8 (~PD), U7.7 (V+), U7.8 (~PD), U8.4 (V+), U9.4 (V+), U10.4 (V+), U11.4 (V+)
+33.1V: +33V1.1, C7.1, J13.1 (In), R3.1, R7.1, R8.1, R9.1, R10.1, U2.1 (OUT), U2.20 (OUT)
+34.3V: +34V3.1, C1.2, C4.1, C5.1, R2.2, U1.5 (VOUT), U2.13 (EN), U2.15 (IN), U2.16 (IN)
/amplifiers/AOUT1: J6.1 (In), R23.2, U8.1 (-)
/amplifiers/AOUT2: J4.1 (In), R24.2, U9.1 (-)
/amplifiers/AOUT3: J3.1 (In), R25.2, U10.1 (-)
/amplifiers/AOUT4: J2.1 (In), R26.2, U11.1 (-)
/amplifiers/DOUT1: J7.1 (In), J12.2, R31.2, U8.5
/amplifiers/DOUT2: J8.1 (In), J12.3, R32.2, U9.5
/amplifiers/DOUT3: J10.1 (In), J12.6, R33.2, U10.5
/amplifiers/DOUT4: J11.1 (In), J12.5, R34.2, U11.5
/amplifiers/IN1: C27.1, D1.2 (A), R15.1, R19.1
/amplifiers/IN2: C28.1, D2.2 (A), R16.1, R20.1
/amplifiers/IN3: C29.1, D3.2 (A), R17.1, R21.1
/amplifiers/IN4: C30.1, D4.2 (A), R18.1, R22.1
GND: C2.2, C3.2, C4.2, C5.2, C6.2, C7.2, C8.2, C9.2, C10.2, C11.2, C12.2, C13.2, C14.2, C15.2, C16.2, C17.2, C18.2, C19.2, C20.2, C21.2, C22.2, C23.2, C24.2, C25.2, C26.2, C31.2, C32.2, C33.2, C34.2, C35.2, C36.2, C37.2, C38.2, C39.2, C40.2, C41.2, C42.2, C43.2, C44.2, C45.2, C46.2, C47.2, C48.2, C49.2, C50.2, H1.1, H2.1, H3.1, H4.1, H5.1, H6.1, H7.1, H8.1, H9.1, H10.1, H11.1, H12.1, J1.1, J1.2, J1.3, J1.4, J1.5, J1.6, J2.2 (Ext), J3.2 (Ext), J4.2 (Ext), J5.1, J5.2, J5.3, J5.4, J5.5, J5.6, J6.2 (Ext), J7.2 (Ext), J8.2 (Ext), J9.1, J9.2, J9.3, J10.2 (Ext), J11.2 (Ext), J12.1, J13.2 (Ext), R1.1, R4.2, R6.2, U1.2 (GND), U2.2 (NC), U2.7 (GND), U2.17 (NC), U2.18 (NC), U2.19 (NC), U2.21 (EP), U3.2 (NC), U3.7 (GND), U3.8 (1.6V), U3.10 (0.4V), U3.17 (NC), U3.18 (NC), U3.19 (NC), U3.21 (EP), U4.5 (V-), U4.9 (V-), U5.5 (V-), U5.9 (V-), U6.5 (V-), U6.9 (V-), U7.5 (V-), U7.9 (V-), U8.2 (V-), U8.6 (SHDN), U9.2 (V-), U9.6 (SHDN), U10.2 (V-), U10.6 (SHDN), U11.2 (V-), U11.6 (SHDN)
unnamed: C11.1, R7.2, R11.1
unnamed: C12.1, R8.2, R12.1
unnamed: C13.1, R9.2, R13.1
unnamed: C14.1, R10.2, R14.1
unnamed: C15.1, C19.1, C23.1, D1.1 (K), R11.2
unnamed: C16.1, C20.1, C24.1, D2.1 (K), R12.2
unnamed: C17.1, C21.1, C25.1, D3.1 (K), R13.2
unnamed: C18.1, C22.1, C26.1, D4.1 (K), R14.2
unnamed: R23.1, U4.6
unnamed: R24.1, U5.6
unnamed: R25.1, U6.6
unnamed: R26.1, U7.6
unnamed: C1.1, R1.2, R2.1, U1.3 (FB)
unnamed: L1.1, U1.1 (SW)
unnamed: C6.1, U2.14 (NR)
unnamed: R3.2, R4.1, U2.3 (SENSE/FB)
unnamed: C9.1, U3.14 (NR)
unnamed: R15.2, U4.3 (-)
unnamed: C27.2, R19.2, U4.1 (FB)
unnamed: R16.2, U5.3 (-)
unnamed: C28.2, R20.2, U5.1 (FB)
unnamed: R17.2, U6.3 (-)
unnamed: C29.2, R21.2, U6.1 (FB)
unnamed: R18.2, U7.3 (-)
unnamed: C30.2, R22.2, U7.1 (FB)
unnamed: R27.1, R31.1, U8.3 (+)
unnamed: R28.1, R32.1, U9.3 (+)
unnamed: R29.1, R33.1, U10.3 (+)
unnamed: R30.1, R34.1, U11.3 (+)

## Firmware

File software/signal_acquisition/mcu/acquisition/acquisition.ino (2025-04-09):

// serial communications
// #define DEBUG
#define START_FLAG 0x7E
#define END_FLAG 0x7D

// hardware interrupt
#define TRIGGER 2
volatile bool triggered = false;
#define MANUAL_RESET 3
volatile bool resetted = false;
#define RESET 4

// FPGA data shifting
#define CS 10
#define MISO 12
#define CLK 13

void setup() {
  // Serial communication w/ computer and software
  Serial.begin(115200);

  // hardware interrupt for trigger
  pinMode(TRIGGER, INPUT);
  attachInterrupt(digitalPinToInterrupt(TRIGGER), trigger, RISING);

  // auto reset
  pinMode(MANUAL_RESET, INPUT_PULLUP);
  attachInterrupt(digitalPinToInterrupt(MANUAL_RESET), reset, FALLING);

  pinMode(RESET, OUTPUT);
  digitalWrite(RESET, HIGH);

  // FPGA data shifting
  pinMode(CS, OUTPUT);
  digitalWrite(CS, HIGH);

  pinMode(MISO, INPUT);
  pinMode(CLK, OUTPUT);
  digitalWrite(CLK, LOW);
}

void loop() {
  if (triggered) {
    // delayMicroseconds(30);
    // Start SPI transaction
    digitalWrite(CS, LOW); // Select FPGA

    uint32_t value = 0;
    for (int i = 0; i < 24; i++) {
      digitalWrite(CLK, HIGH);
      digitalWrite(CLK, LOW);

      value <<= 1;
      value |= digitalRead(MISO);
    }
    
    digitalWrite(CS, HIGH); // Deselect FPGA

#ifdef DEBUG
    Serial.print("TRIGGERED: 0x");
    Serial.println(value, HEX);
#endif
#ifndef DEBUG
    Serial.write(0x00);
    Serial.write(0x00);
    Serial.write(START_FLAG);
    Serial.write((uint8_t*)&value, 4);
    Serial.write(END_FLAG);
    Serial.write(0x00);
    Serial.write(0x00);
#endif

    triggered = false;

    reset();
  }

  if (resetted) {
    digitalWrite(RESET, LOW);
    digitalWrite(RESET, HIGH);
  }
}

void trigger() {
  triggered = true;
}

void reset() {
  resetted = true;
}

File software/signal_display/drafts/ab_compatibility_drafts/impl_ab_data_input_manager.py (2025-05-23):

import os
import struct

from datetime import datetime

import serial
import numpy as np

from OpenGL.GL import *

from scintillator_display.math.convex_hull import ConvexHullDetection as Detection

from scintillator_display.universal_values import MathDisplayValues

from scintillator_display.display.vao_vbo import create_vao, update_vbo, draw_vao

class Data(MathDisplayValues):
    def __init__(self, impl_constant, impl, hull_colour, hull_opacity, store_normals, debug=True):
        self.debug = debug
        self.impl = impl # "a" or "b"
        self.hull_colour = hull_colour
        self.hull_opacity = hull_opacity
        self.store_normals = store_normals
        self.data = []
        self.impl_a_data_is_checked = []
        self.impl_b_data_is_checked = []
        self.detection_algorithm = Detection(impl_constant=impl_constant)



        if self.debug:
            self.testing()
            pass
        else:
            if os.name == "nt":
                dsrdtr = True
                port = "COM5"
            else:
                dsrdtr = False
                port = "/dev/ttyUSB0"

            self.arduino = serial.Serial(port=port, baudrate=115200, dsrdtr=dsrdtr)


    def arduino_has_data(self):
        if self.debug:
            return False
        return self.arduino.in_waiting >= 8
    
    def get_data_from_arduino(self):
        """
        Gather the data from Arduino
        """
        self.arduino.read_until(b"\x7E")
        value = self.arduino.read(4)
        if self.arduino.read(1) != b"\x7D":
            print("serial frame end error")

        (n,) = struct.unpack("<I", value)

        return n
    
    
    def format_print(self, value):
        lsb = value & 0xFFFFFF
        b1 = (lsb >> 16) & 0xFF
        b2 = (lsb >> 8) & 0xFF
        b3 = lsb & 0xFF

        print("receive trigger: SiPM status")
        print(f"    {b1:02x}          {b2:02x}          {b3:02x}")
        print(f"    {b1:08b}    {b2:08b}    {b3:08b}")
        print()

    def num_to_raw_binary(self, num):
        return np.array([(num & (2**i)) >> i for i in range(24)])
    
    
    def cook_data_into_scintillators(self, raw_data):
        """
        transform data ready to be interpreted by the display, then update self.data
        """
        
        f_sc_idx = [
        [(21,20),(16,17),(13,12),(8,9),(0,1),(5,4),],
        [(22,23),(18,19),(15,14),(11,10),(2,3),(6,7),],
        ]

        k = self.num_to_raw_binary(raw_data)[f_sc_idx]

        cooked_data = [[(int(k[0]), int(k[1])) for k in k[0]], [(int(k[0]), int(k[1])) for k in k[1]]]

        return cooked_data
    
    def is_valid_data(self, data=None):
        self.raw_data = self.get_data_from_arduino() if data==None else data
        self.cooked_data = self.cook_data_into_scintillators(self.raw_data)
        self.scintillator_bounds = self.detection_algorithm.scintillators_to_bounds(self.cooked_data)

        if self.impl == "a":
            if not self.scintillator_bounds:
                return
            elif self.scintillator_bounds == None:
                return
        elif self.impl == "b":
            if self.scintillator_bounds == None:
                return False
            return True


    def scale_hull_bounds(self, hull_bounds):
        '''
        hull_bounds = [1, 2, 3, 4, 5, 6, 7, 8]
        '''

        idx = [[0, 7],[1, 6],[2, 5],[3, 4]]
        fan = np.array(hull_bounds)[idx]
        scale_factor = 75 if self.impl == "a" else 700 if self.impl == "b" else 0
        fan_vec = np.array([scale_factor*(p[0]-p[1])/np.linalg.norm(p[0]-p[1]) for p in fan])
        
        scaled_p0 =  fan_vec[0]+hull_bounds[0]
        scaled_p1 =  fan_vec[1]+hull_bounds[1]
        scaled_p2 =  fan_vec[2]+hull_bounds[2]
        scaled_p3 =  fan_vec[3]+hull_bounds[3]
        scaled_p4 = -fan_vec[3]+hull_bounds[4]
        scaled_p5 = -fan_vec[2]+hull_bounds[5]
        scaled_p6 = -fan_vec[1]+hull_bounds[6]
        scaled_p7 = -fan_vec[0]+hull_bounds[7]


        scaled_hull_bounds = [scaled_p0, scaled_p1,
                              scaled_p2, scaled_p3,
                              scaled_p4, scaled_p5,
                              scaled_p6, scaled_p7]

        return scaled_hull_bounds
        
    
    def transform_data_per_impl(self):
        hull_bounds = self.scintillator_bounds

        time = datetime.now()

        if self.impl == "a":
            new_hull_bounds = self.transform_coordinates_impl_a(hull_bounds)
        elif self.impl == "b":
            new_hull_bounds = np.array(hull_bounds) - np.array([0, 0, self.SPACE_BETWEEN_STRUCTURES/2])



        bit24 = self.raw_data & 0xffffff
                
        point = [new_hull_bounds, self.cooked_data, bit24, time]

        self.data.append(point)
        self.impl_a_data_is_checked.append(False)
        self.impl_b_data_is_checked.append(False)

        
            
        if self.impl == "b":
            return np.array(new_hull_bounds).astype(np.float32)


    def transform_coordinates_impl_a(self,data):
        """
        transform into my coordinate system
        """
        translate_x = -self.detection_algorithm.n / 2
        translate_y = -self.detection_algorithm.n / 2
        z_scale = 1

        lst = []
        for i, coordinates in enumerate(data):
            x = (coordinates[0] + translate_x) * -1
            y = (coordinates[1] + translate_y) *  1
            z = (coordinates[2] + self.detection_algorithm.half_gap_size - self.detection_algorithm.inter_level_gap + self.detection_algorithm.plate_thickness) / z_scale
            lst.append((x,y,z))

        return lst
    

    def make_points_from_high_low(self, xl, xh, yl, yh, zl, zh, colour=[], opacity=[]):
        points = np.array([
            np.array([xl, yl, zl, *colour, *opacity]), # base_point + (0,    0,    0)    # BFL
            np.array([xh, yl, zl, *colour, *opacity]), # base_point + (xlen, 0,    0)    # BFR
            np.array([xl, yh, zl, *colour, *opacity]), # base_point + (0,    ylen, 0)    # BBL
            np.array([xh, yh, zl, *colour, *opacity]), # base_point + (xlen, ylen, 0)    # BBR
            np.array([xl, yl, zh, *colour, *opacity]), # base_point + (0,    0,    zlen) # TFL
            np.array([xh, yl, zh, *colour, *opacity]), # base_point + (xlen, 0,    zlen) # TFR
            np.array([xl, yh, zh, *colour, *opacity]), # base_point + (0,    ylen, zlen) # TBL
            np.array([xh, yh, zh, *colour, *opacity]), # base_point + (xlen, ylen, zlen) # TBR
        ])
        return points
    

    def make_prism_triangles(self, p1, p2, p3, p4, p5, p6, p7, p8, show_top_bottom=False):

        '''
        one base has changing basepoints and x_increment of rod width
        one base has fixed basepoint and square side length increment
        z starts from box base z and add box z increment
        '''

        # front face
        tf1 = [p1, p2, p5]
        tf2 = [p2, p5, p6]

        # back face
        tb1 = [p3, p4, p7]
        tb2 = [p4, p7, p8]
        
        # left face
        tl1 = [p1, p3, p5]
        tl2 = [p3, p5, p7]

        # right face
        tr1 = [p2, p4, p6]
        tr2 = [p4, p6, p8]

        all_t = []

        all_t.extend(tf1)
        all_t.extend(tf2)
        all_t.extend(tb1)
        all_t.extend(tb2)
        all_t.extend(tl1)
        all_t.extend(tl2)
        all_t.extend(tr1)
        all_t.extend(tr2)


        if show_top_bottom:
            # bottom face
            tB1 = [p1, p2, p3]
            tB2 = [p2, p3, p4]
            # top face
            tT1 = [p5, p6, p7]
            tT2 = [p6, p7, p8]
            all_t.extend(tB1)
            all_t.extend(tB2)
            all_t.extend(tT1)
            all_t.extend(tT2)

        return all_t    

    def hull_setup_for_data_point(self, hull_bounds, hull_colour, hull_opacity, show_top_bottom=False):
        vertices = []

        scaled_hull_bounds = self.scale_hull_bounds(hull_bounds)
        
        centre_prism = self.make_prism_triangles(*hull_bounds, show_top_bottom)
        vertices.extend(centre_prism)

        top_triangle_fans = self.make_prism_triangles(*hull_bounds[:4], *scaled_hull_bounds[:4], show_top_bottom)
        vertices.extend(top_triangle_fans)

        bottom_triangle_fans = self.make_prism_triangles(*hull_bounds[4:], *scaled_hull_bounds[4:], show_top_bottom)
        vertices.extend(bottom_triangle_fans)

        vertices = np.array(vertices, dtype = np.float32)

        vd = np.ones((len(vertices), 10), dtype=np.float32)
        vd[:, :3]   = vertices
        vd[:, 3:6]  = hull_colour
        vd[:, 6]    = hull_opacity
        vd[:, 7:10] = vertices

        #if self.impl == "a":
        #    vd = np.ones((len(vertices), 10), dtype=np.float32)
        #    vd[:, :3]   = vertices
        #    vd[:, 3:6]  = hull_colour
        #    vd[:, 6]    = hull_opacity
        #    vd[:, 7:10] = vertices
        #elif self.impl == "b":
        #    vd = np.ones((len(vertices), 7), dtype=np.float32)
        #    vd[:, :3]   = vertices
        #    vd[:, 3:6]  = hull_colour
        #    vd[:, 6]    = hull_opacity

        return vd
    

    def create_hull_data_and_vao(self, hull_bounds):
        hull_data = self.hull_setup_for_data_point(
            hull_bounds, self.hull_colour, self.hull_opacity)
        hull_vao = create_vao(hull_data, store_normals=self.store_normals)
        n = hull_data.shape[0]
        return hull_vao, n
    
    def draw_active_hulls(self, data_points, data_active):
        if data_points == []:
            return
        else:
            for i, j in enumerate(data_active):
                if j == True:
                    hull_bounds = data_points[i][0]
                    vao, n = self.create_hull_data_and_vao(hull_bounds)
                    draw_vao(vao, GL_TRIANGLES, n)
    
    def testing(self):
        test_data = [
                0b011011010110101011010110,
                0b100110101101010101101001,
                0b100101101010011101011001,
                1431655765,
                #2**33 - 1
            ]
        for data in test_data:
            self.is_valid_data(data)
            self.transform_data_per_impl()

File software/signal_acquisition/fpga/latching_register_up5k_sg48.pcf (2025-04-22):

# Assign parallel input data lines

# shifter set 1
set_io S[23] 139
set_io S[22] 144
set_io S[21] 143
set_io S[20] 142
set_io S[19] 141
set_io S[18] 64
set_io S[17] 63
set_io S[16] 62

# shifter set 2
    #set_io S[15] 61
    #set_io S[14] 60
    #set_io S[13] 58
    #set_io S[12] 56
    #set_io S[11] 52
    #set_io S[10] 50
    #set_io S[9] 138 # 49 blocked for PLL
    #set_io S[8] 48  #

set_io S[15] 61 #
set_io S[14] 60 #
set_io S[13] 58 #
set_io S[12] 56 #

set_io S[11] 50 #
set_io S[10] 138 # 49 blocked for PLL
set_io S[9] 52  #
set_io S[8] 48  #

# shifter set 3
set_io S[7] 47  #
set_io S[6] 45  #
set_io S[5] 39  #
set_io S[4] 44  #
set_io S[3] 43  #
set_io S[2] 42  #
set_io S[1] 41  #
set_io S[0] 38  #


# PLL signals
set_io sys_clk 73
set_io sys_clk_pll 1
set_io sys_clk_pll_lock 114


# stm32 data signals
set_io rst_n 34
set_io trigger 8

set_io spi_cs 7
set_io spi_miso 2
set_io spi_clk 4


# debug signals
set_io counter_0 9
set_io counter_1 3
set_io trigger_led 113

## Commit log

2025-02-23 SiPM breakout board
    [sipm.kicad_pcb, sipm.kicad_sch]
2025-02-23 finalized SiPM PCB
    [sipm.kicad_pcb, sipm.kicad_sch]
2025-02-24 arduino testing
2025-02-27 power PCB
    [power.kicad_pcb, power.kicad_sch]
2025-02-27 sipm PCB updates
2025-02-27 refactor power
    [power.kicad_pcb, power.kicad_sch]
2025-02-27 fix ground planes
    [power.kicad_pcb]
2025-02-28 run drc
    [power.kicad_pcb]
2025-03-14 trigger pcb
    [trigger.kicad_pcb, trigger.kicad_sch]
2025-03-15 trigger pcb rework
    [amplifiers.kicad_sch, power.kicad_sch, sensors.kicad_sch, trigger.kicad_sch]
2025-03-15 conclude schematic
    [amplifiers.kicad_sch, power.kicad_sch, sensors.kicad_sch, trigger.kicad_sch]
2025-03-15 pcb v1
    [amplifiers.kicad_sch, power.kicad_sch, sensors.kicad_sch, trigger.kicad_pcb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]
2025-03-17 finalize pcb
    [trigger.kicad_pcb]
2025-03-18 pcb fabrication files
    [amplifiers.kicad_sch, power.kicad_sch, sensors.kicad_sch, trigger.kicad_pcb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]
2025-03-19 acquisition pcb
    [acquisition.kicad_pcb, acquisition.kicad_sch, fpga.kicad_sch, mcu.kicad_sch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]
2025-03-20 fix trigger pcb
    [amplifiers.kicad_sch, power.kicad_sch, trigger.kicad_pcb, trigger.kicad_sch]
2025-03-20 update to opa858
    [amplifiers.kicad_sch, power.kicad_sch, sensors.kicad_sch, trigger.kicad_pcb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]
2025-03-20 fabrication for trigger
    [trigger-B_Cu.gbl, trigger-B_Mask.gbs, trigger-B_Paste.gbp, trigger-B_Silkscreen.gbo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]
2025-03-26 Create bl4s_proposal.tex
    LaTeX file containing the Scintilating Chamber BL4S proposal. Updated regularly from Proposal.doc on the Google Drive repository: https://drive.google.com/drive/folders/19_MMcoH1Qw7MvBGZwiW7HJuY0r8M6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
2025-03-28 Famework and rename bl4s_proposal.tex to main.tex
    Added some of the framework for the main file.
2025-04-06 pins of registers
    [acquisition.kicad_sch, untitled.kicad_sch]
2025-04-06 arduino code
2025-04-08 arduino input for display_1
2025-04-09 data input & camera clipping
2025-04-10 refactor hardware
    [acquisition.PcbDoc, acquisition.PrjPcb, acquisition.SchDoc, acquisition.kicad_pcb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]
2025-04-12 testing gitignore
    [2025-04-11 22:39:48.778073.csv]
2025-04-12 cleanup tree
    [2025-04-11 22:39:48.778073.csv]
2025-04-16 impl a and b data manager and arduino in single file, compatible for both
2025-04-16 long term print
2025-04-20 universal camera, shaders for both
2025-04-21 new hardware
    [acquisition.PcbDoc, acquisition.PrjPcb, acquisition.SchDoc, acquisition.kicad_pcb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]
2025-04-23 acquisition v2 basics
    [acquisition.kicad_sch, fpga.kicad_sch, power.kicad_sch]
2025-04-23 24 mhz oscillator
    [fpga.kicad_sch]
2025-05-07 fixed 1.57 million vao creation effect, added DataPoint class, fixed data column length issue between demo and debug
2025-06-17 First parts of the aquisition pcb design
    [acquisition.kicad_pcb, acquisition.kicad_sch, fpga.kicad_sch, mcu.kicad_sch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]
2025-06-18 Small changes on all sheets
    [fpga.kicad_sch, mcu.kicad_sch, power.kicad_sch]
2025-06-30 Added the DAC/ADC array for analog conversion.
    Added an array of 6 quad-channels DAC with I2C interface to control the threshold voltage of a set of 12 dual channel ADCs. Loose, general wiring of FPGA and MCU present, detailed schematics in the w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
    [acquisition.kicad_sch, amplifiers.kicad_sch, converters.kicad_sch, digital.kicad_pcb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]
2025-07-02 Added SD card readers and USB-C for power in.
    [converters.kicad_sch, converters2.kicad_sch, digital.kicad_sch, fpga.kicad_sch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]
2025-07-03 generate pdfs
    [amplifiers.kicad_sch, digital.kicad_sch, power.kicad_sch, sensors.kicad_sch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]
2025-07-09 Small aesthetic changes and small rework of power sheet.
    [converters.kicad_sch, digital.kicad_sch, fpga.kicad_sch, power.kicad_sch]
2025-07-09 add power redundancy with OR-ing controller
    [power.kicad_sch]
2025-07-10 complete power
    [digital.kicad_sch, power.kicad_sch, power_sipm.kicad_sch, usb.kicad_sch]
2025-07-11 reroute dac + comparators
    [comparators.kicad_sch, dac.kicad_sch, digital.kicad_sch, mcu.kicad_sch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]
2025-07-11 series resistors
    [comparators.kicad_sch, dac.kicad_sch, power_sipm.kicad_sch, usb.kicad_sch]
2025-07-11 annotate dip switches
    [comparators.kicad_sch, dac.kicad_sch, power_sipm.kicad_sch, usb.kicad_sch]
